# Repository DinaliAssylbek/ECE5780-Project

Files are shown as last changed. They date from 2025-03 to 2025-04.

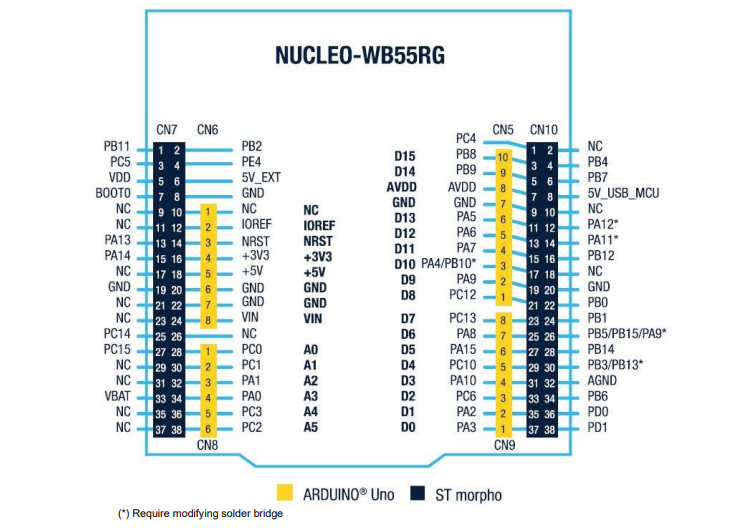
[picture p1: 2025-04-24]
Photos/DEV_Board Pinout.png

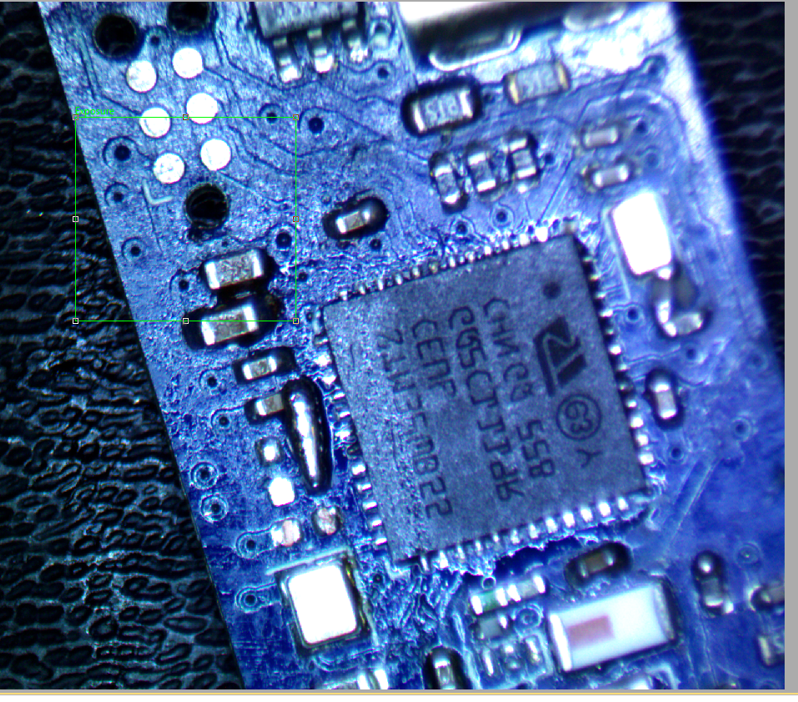
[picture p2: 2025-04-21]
Photos/Screenshot 2025-04-17 140008.png

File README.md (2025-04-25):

Team Members:
Hayden Walpole; Undergraduate; Computer Engineering 
Andy Tran; Undergraduate; Computer Engineering 
Dinali Assylbek; Undergraduate; Computer Engineering
Stein Witt; Undergraduate; Mechanical Engineering

-File Directory-
CAD_FILES: file for the Platic Housing of our Watch Monitor
Datasheetes: BOM and datasheets for the given componants
HealthMonitor: Main Code file to be used to Flash the board with initialization and reading the sensor
Nucleo_Board_Testing: Code used to Test Dev board and Flashing with our 6-pin SWD cable.
PCB: PCB Scematic files and Board Design
Photos: Pictures of the development and debugging process. Also contains helpful refrence photos
Analog Discovery Code Attempts: Code we tried to use to communicate over I2C using Waveform with an analog discovery.

Milestone 4 Powerpoint presentation: https://1drv.ms/p/c/c447666567076377/EbAtq3pLUSZKpYCg5cf9b-IBzeUnjeowH9_FPiCp1k7Zxw?e=1KSI1v

You need to install the following for the STM32 VSCode extension to work.

-STMCubeIDE
-STMCubeMX
-STMCLT
-STMMCU
ECE 5780 – ReadMe Documentation
Project Name: Wearable Health Monitor 
Purpose:
The purpose of this project is to design, assemble, and program a custom PCB for a compact wearable device that allows a person to continuously monitor their heart rate and blood oxygen levels (SpO₂). The device provides real-time feedback when readings fall outside safe thresholds by using an onboard vibrating motor and status LEDs. It is intended to be a low-power, discreet health monitoring solution suitable for everyday use.
Functionality:
The Wearable Health Monitor includes the following features:
•	Real-Time Heart Rate Monitoring: Uses the MAX30102 optical sensor to continuously measure the user’s heart rate.
•	SpO₂ (Blood Oxygen) Monitoring: Calculates and updates the user’s oxygen saturation level every few seconds.
•	Vibration Motor and Status LED: Activates when heart rate or oxygen levels are outside the defined safe range.
•	Power Supply: Currently powered via USB-C. However, the board can run on a battery if connected through the USB-C port (e.g., with a USB-C battery pack).

•	Optional Bluetooth: The board supports Bluetooth; however, Bluetooth functionality is not implemented in the driver code.

Setup Instructions:
1.	PCB Fabrication:
To manufacture the board, use the schematic and PCB layout files found in the PCB directory of the GitHub repository. These files are compatible with common PCB manufacturers such as PCBWay (used for this project). Before submission, make sure to generate and include:
o	Gerber files
o	Bill of Materials (BOM)
o	Pick-and-place files (if needed)
The schematic for this project is presented below: 
 
2.	Assembly Guidelines:
Component assembly is a critical step due to the small form factor and use of QFN or similar packages that do not expose all pins. Many components have pads located underneath, making traditional soldering difficult.
Important:
Avoid using a reflow oven. While convenient, reflow can result in unreliable connections or floating components. Instead:
o	Use solder paste with a precision heat gun
o	Inspect each connection carefully under magnification
However, if your manufacturer offers services for PCB assembly, it is advisable to have them assemble the board for you. This is to avoid any potential problems regarding the PCB itself.
Note: Be careful when handling the board after assembly, the parts are delicate!
3.	Programming the Board:
The board is programmed using a dedicated ST-Link programmer with a 6-pin Tag-Connect cable.
o	To enter bootloader mode:
	Power the board
	Press and hold the BOOT button
	Momentarily ground the NRST (reset) pin (accessible via the ST-Link header)
	Release NRST while continuing to hold BOOT for a few seconds
Note: While USB-C bootloader programming is theoretically possible, it has not been tested. The ST-Link method is the recommended and verified approach.
When using the ST-Link, bootloader mode is not required.
4.	Firmware Setup:
o	Clone the repository and open the Health Monitor project
o	All source files are in the Core directory
o	A custom library for the MAX30102 sensor is included
Pin Configuration:
o	PB8 → I2C1_SCL (Clock Line)
o	PB9 → I2C1_SDA (Data Line)
o	Pin 12 → Controls both the vibration motor and status LED
The project builds and runs best using the STM32CubeIDE and STM32CubeProgrammer.
Once the board is powered and connected via ST-Link:
o	Build the project
o	Flash the firmware using the programmer
o	The device will begin operation immediately after flashing

5.	Troubleshooting
In the case where you may encounter issues with the PCB, there are several steps you can take to diagnose and resolve problems:
o	No Power to the Board:
o	Confirm that the USB-C cable is securely connected and providing power. If not, try to use a different cable to supply power to the chip
o	Check the voltages along all the voltage lines (3.3V and 1.8V) using a multimeter.
o	Ensure all power-related components (LDO regulator, bypass caps, etc.) are properly soldered. If the board starts to heat up rapidly, use a thermal camera to help check for shorts.
o	Sensor Not Detected (MAX30102):
o	Double-check I2C connections (PB8 for SCL, PB9 for SDA).
o	Use a logic analyzer or oscilloscope to verify I2C traffic.
o	Confirm the sensor that the registers and addresses are configured correctly.
o	Programming Issues:
o	Make sure the ST-Link is correctly connected via the Tag-Connect header.
o	Ensure that the Tag-Connect and ST-Link work. This can be achieved by uploading code to a breakout board.
o	Ensure that all user code lies in the correct regions as defined in the cube IDE. Check that all the correct header files are included and desired code is not commented out.
o	Miscellaneous Issues:
o	If the PCB fails to work, inspect solder joints again for bridges or incomplete connections. Examine under a microscope. If possible, reach out to someone with a more trained eye to look at the soldering job.
o	Make sure components on the board are assembled correctly. This means making sure the orientations of the components are in the right place, and no components are missing.
o	Be careful when disconnecting the cable when flashing the board. This potentially could cause you to brick the chip on the PCB. 

Videos Used as Refrences:
Schematic Design Video: https://www.youtube.com/watch?v=nkHFoxe0mrU
PBC Design Video: https://www.youtube.com/watch?v=PlXd3lLZ4vc&t=10184s

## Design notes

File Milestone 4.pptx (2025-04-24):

## MILESTONE 1 UPDATE: Integrating Machine Learning Into UTAP App

<N

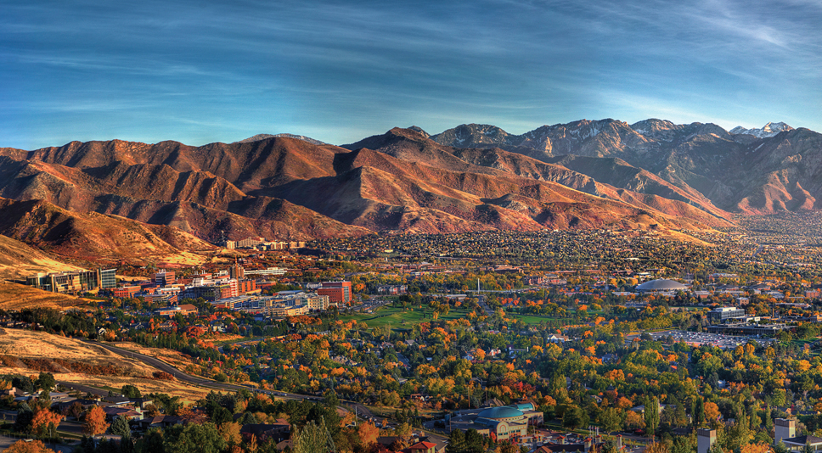
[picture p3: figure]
Campus Fall Panorama

Hayden Walpole and Daniel McNally
Technical Advisor: Nathan Hansen & Prof. Benjamin Sanchez

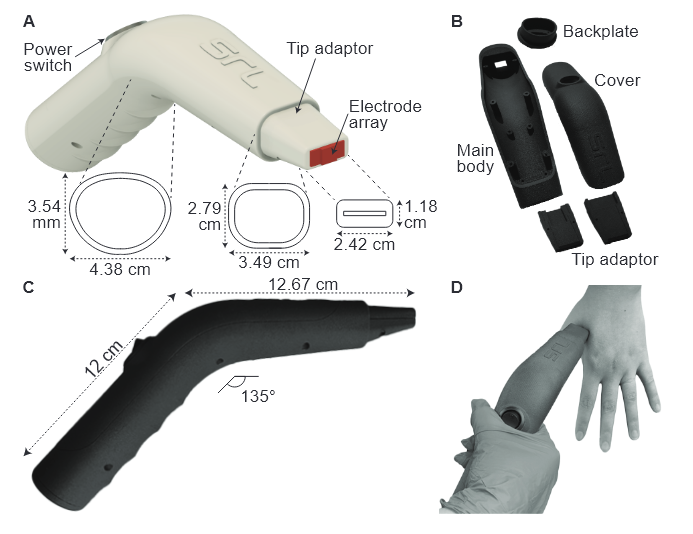
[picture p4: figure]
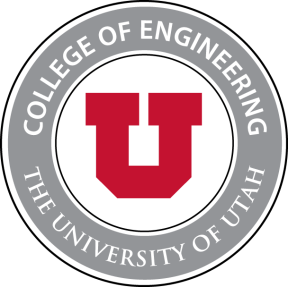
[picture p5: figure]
ENG_SEAL_RedGray

## MILESTONE 1 UPDATE: Integrating Machine Learning Into URSKIN App

<N

Hayden Walpole and Daniel McNally
Technical Advisor: Nathan Hansen & Prof. Benjamin Sanchez

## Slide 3

Our Timeline

Milestone | Estimated Completion
Working Frontend UI | March 15th, 2025
Single Model ML Prototype | April 15th, 2025
Multiple Model ML Application | September 1st, 2025
Final Integrated Application | November 1st, 2025
Demo Day | December 5th, 2025

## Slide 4

Team Contributions

Daniel

User Interface

ONNX Implementation

Hayden

Research: Conversion Tools

Models used in Project
(Slide 8)

CITI Bio-Medical Research Training for Data Collection

ADABoosting Model Testing:
-Default Data Array
-Measure Data from Device

FUTURE:
Data Collection
UI Finalization
Electrode Array Improvement
Individual Model Type Implementation

FUTURE:
Data Collection
Results validation and comparison to PC model
Unit Testing
Multi-Prediction Model

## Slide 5

Original User Interface

User interface changes

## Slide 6

Original User Interface

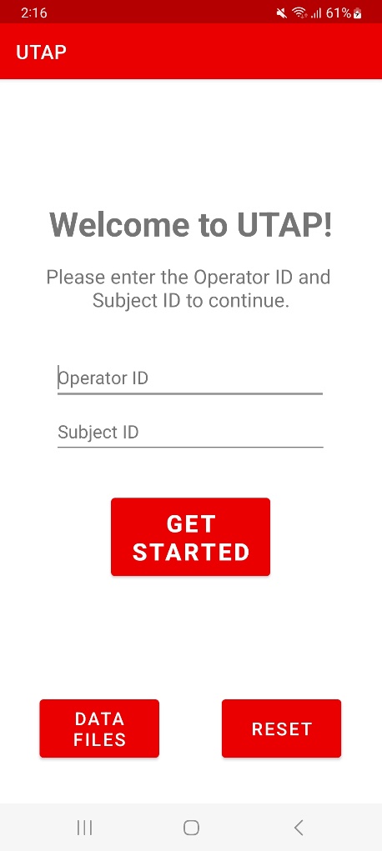
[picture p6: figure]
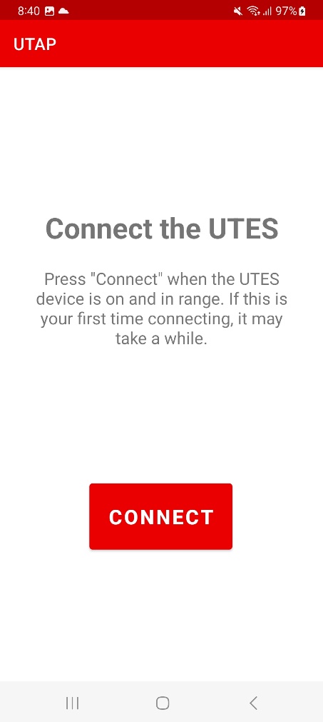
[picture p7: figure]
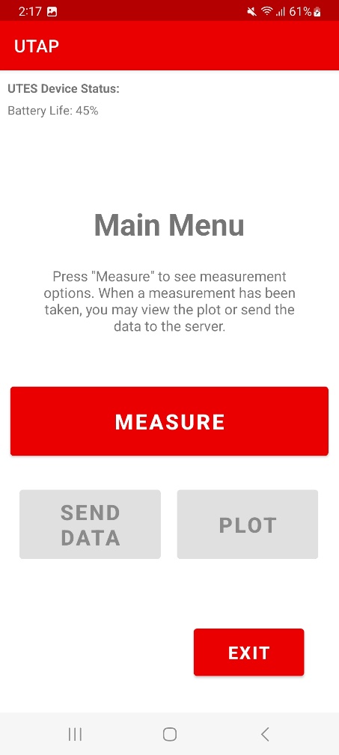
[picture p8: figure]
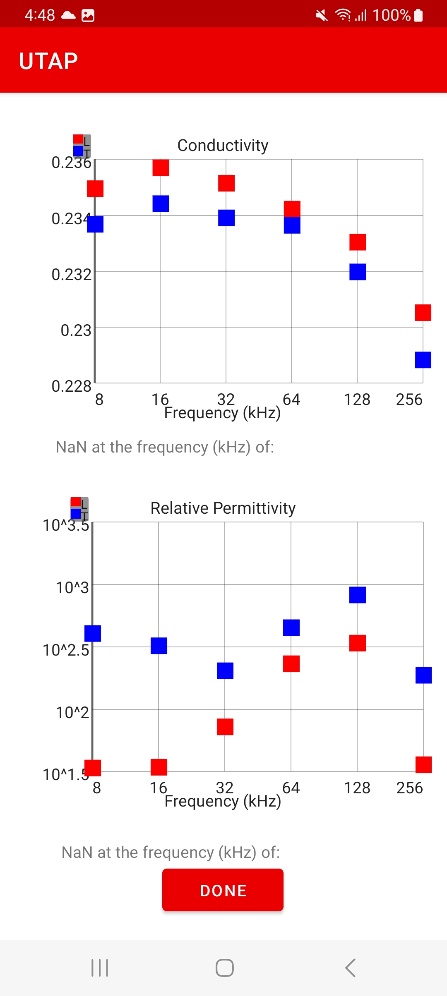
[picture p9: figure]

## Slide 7

New User Interface

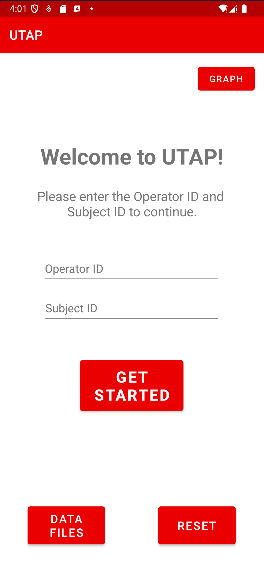
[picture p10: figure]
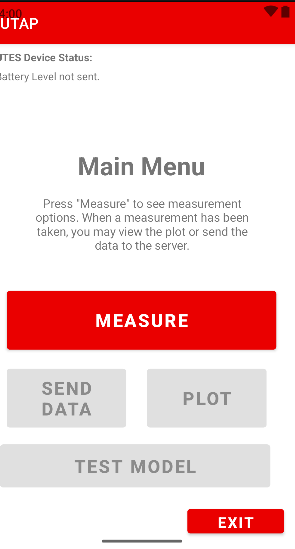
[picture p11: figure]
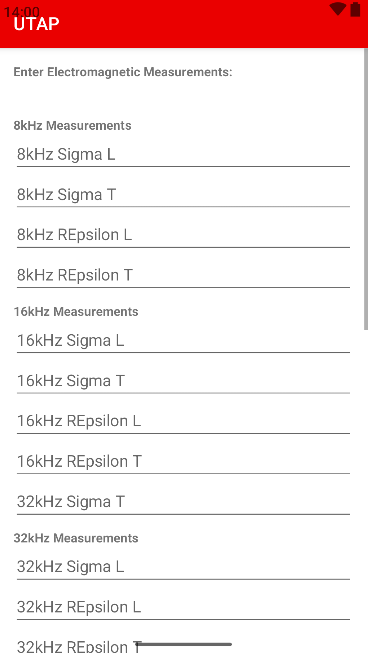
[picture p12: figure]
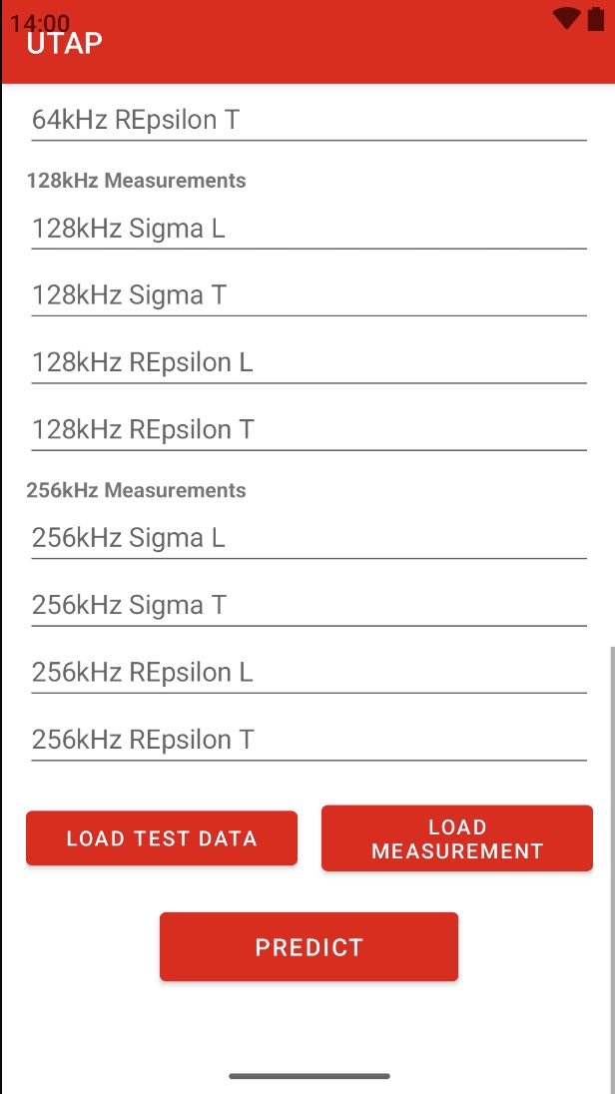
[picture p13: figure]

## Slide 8

Original User Interface

Single Model ML Prototype

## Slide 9

Machine Learning Models Involved

- KNN
- Decision Trees
- Naive Bayes
- Logistic Regression
- Support Vector Machine
- Random Forest
- Adaboosting (base model decision tree stumps)
- Extreme Gradient Boosting (base model decision tree stumps)
- Gradient Boosting (base model decision tree stumps)
- Bagged decision trees
- Voting (based on the best three performing models for each comparison)
- Stacking (based on the best three performing models for each comparison)

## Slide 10

Transferring ML from Python to Mobile app

- One of the first challenges we faced was finding the right conversion process to implement the existing models in Python into our mobile application.
- We decided to use ONNX since it is well documented and well supported for our needs.

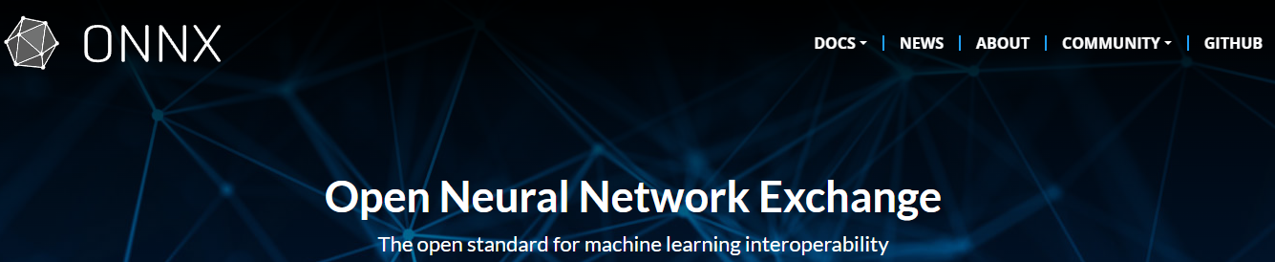
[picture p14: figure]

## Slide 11

Code: Graph Activity

- This was a new class activity we created to import and manage the Models we import from ONNX.

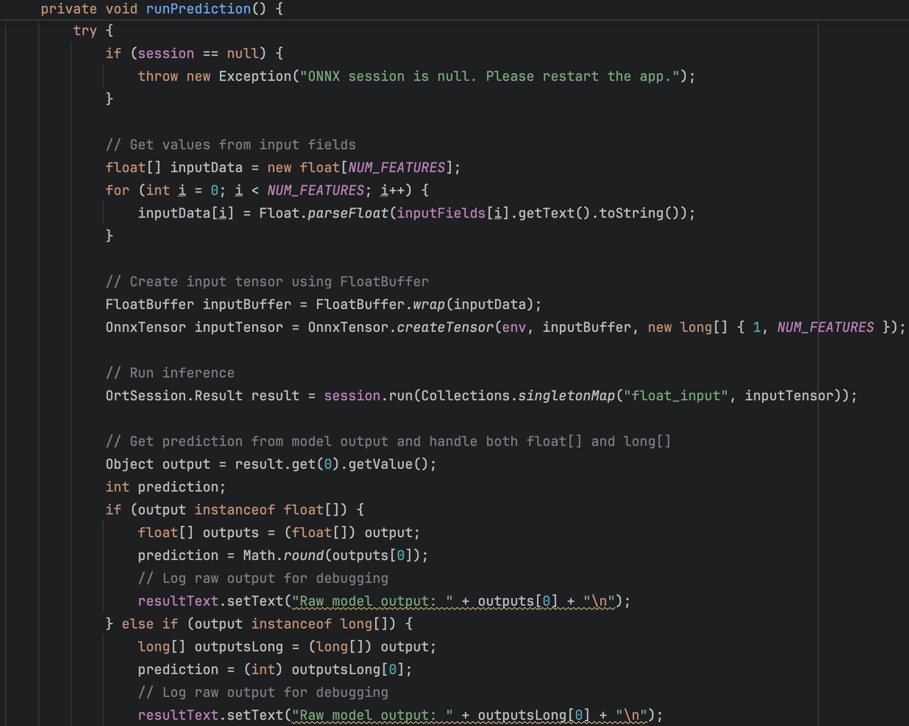
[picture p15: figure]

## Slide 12

Data File

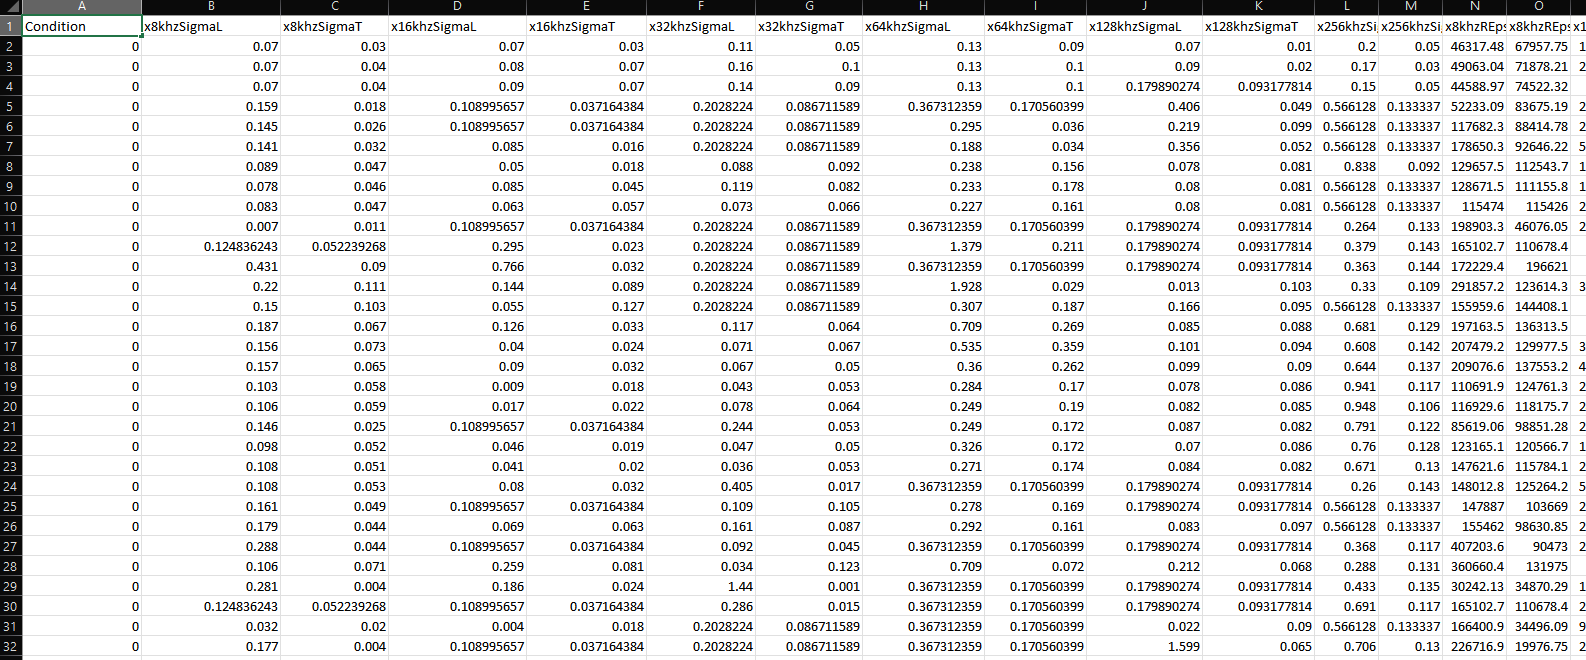
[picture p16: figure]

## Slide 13

Thank You!

ADA BOOSTING DEMO
Healthy Vs SCC

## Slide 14

Plans going Forward

- Our next Steps will be to refine the User interface and integrate more models.
- The models are mostly 1 vs 1 Comparison, so multiple models are required to run the comparisons at once to get the final Prediction.

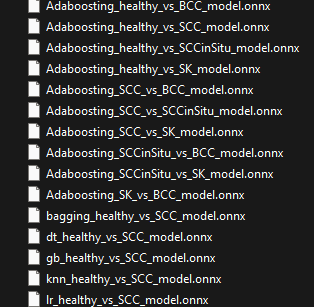
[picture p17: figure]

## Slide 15

Thank You!

Questions?

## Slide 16

Image Sources:

- Images from ONNX mainpage found at https://onnx.ai/
- Images from “UTES Training Guide V6” PowerPoint created by Nathan Hansen
- Images from materials from the Sanchez Research Lab UTES Device Resources and Publications

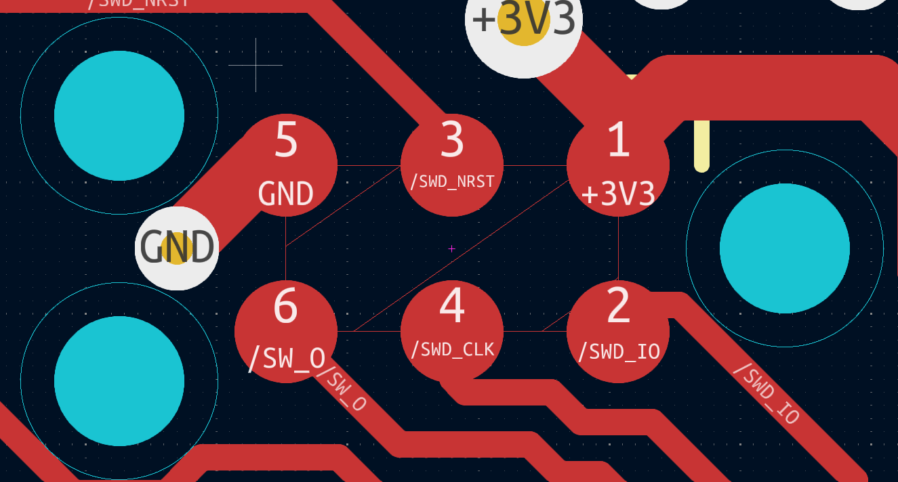
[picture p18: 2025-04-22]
Photos/6-Pin SWD pins.png

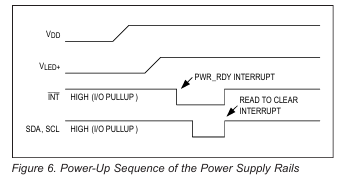
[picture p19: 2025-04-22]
Photos/Sensor Power-up Sequence.png

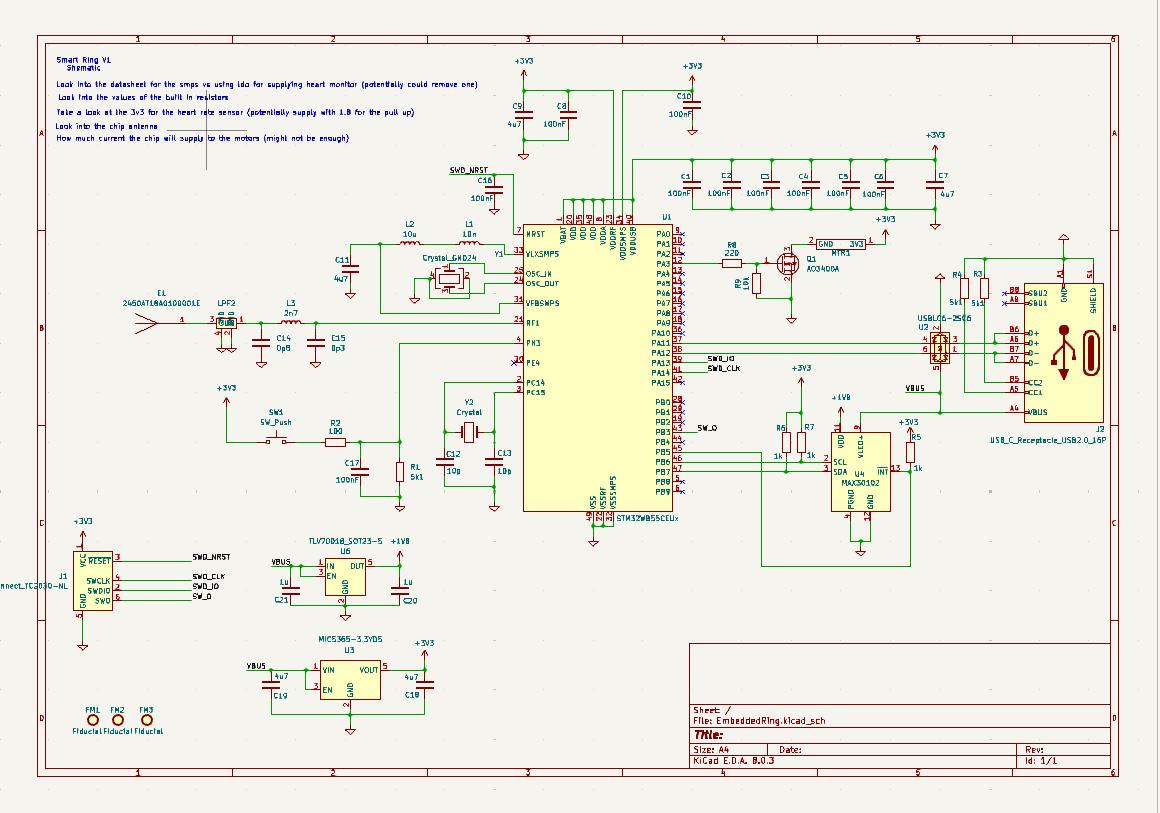
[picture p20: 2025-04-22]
Photos/Full Schemeatic Diagram.png

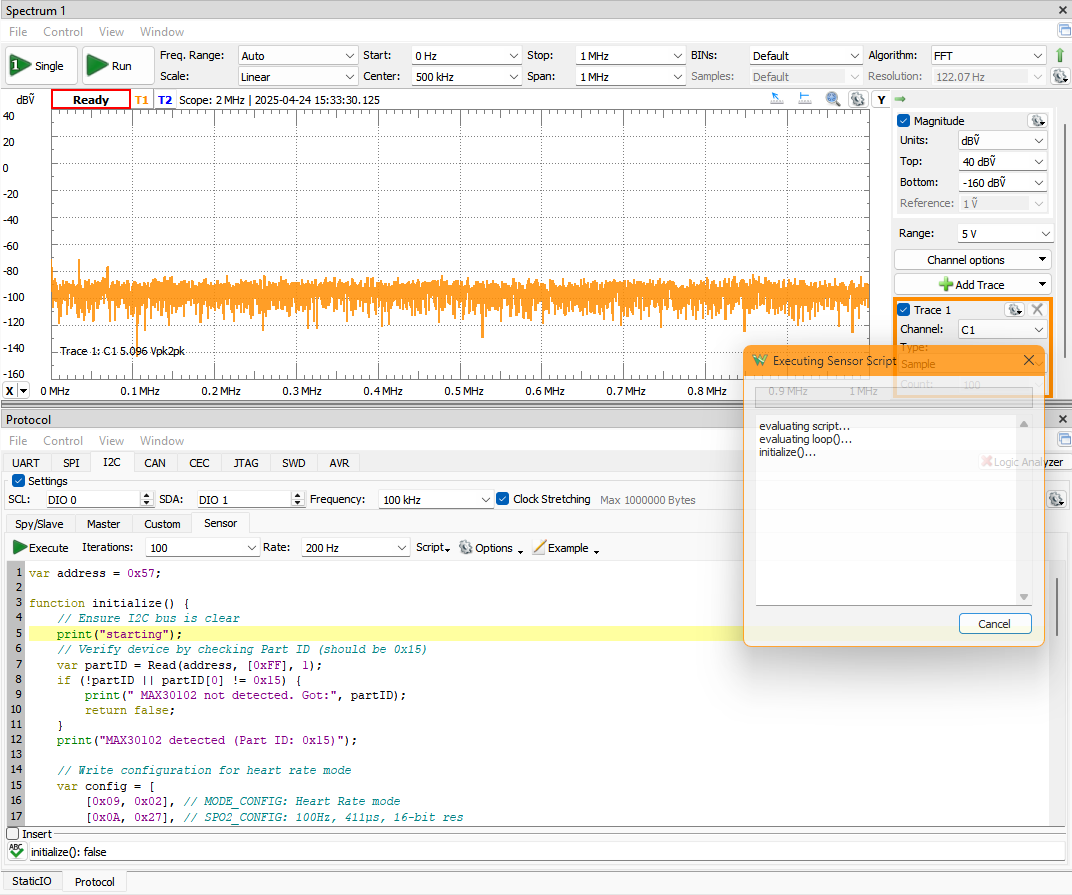
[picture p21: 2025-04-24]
Photos/Analog Waveform I2C attempt.png

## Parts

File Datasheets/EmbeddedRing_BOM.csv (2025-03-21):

Reference | Value | Datasheet | Footprint | Qty | DNP | Distributer Link | Manufacturer | Manufacturer Part Number
LPF2,MTR1 | ~ |  | -- mixed values -- | 2 |  | -- mixed values -- | -- mixed values -- | -- mixed values --
C20,C21 | 1u | ~ | Capacitor_SMD:C_0201_0603Metric_Pad0.64x0.40mm_HandSolder | 2 |  | https://www.digikey.com/en/products/detail/nextgen-components/0603B105K100XD/18677009 | Aillen | 0603B105K100XD
Q1 | AO3400A | http://www.aosmd.com/pdfs/datasheet/AO3400A.pdf | Package_TO_SOT_SMD:SOT-23 | 1 |  | https://www.digikey.com/en/products/detail/alpha-omega-semiconductor-inc/AO3400A/1855772 | Alpha & Omega Semiconductor Inc. | AO3400A
U4 | MAX30102 | https://datasheets.maximintegrated.com/en/ds/MAX30102.pdf | low_pass_filter:heart_rate_sensor | 1 |  | https://www.digikey.com/en/products/detail/analog-devices-inc-maxim-integrated/MAX30102EFD-T/6188734 | Analog Devices Inc./Maxim Integrated | MAX30102EFD+T
SW1 | SW_Push | ~ | Button_Switch_SMD:SW_SPST_CK_RS282G05A3 | 1 |  | https://www.digikey.com/en/products/detail/c-k/RS-282G05A3-SM-RT/2747190?s=N4IgTCBcDaIE4GcwA4wHMAMBWAhgZgQFs4AXEAXQF8g | C&K | RS-282G05A3-SM RT
J2 | USB_C_Receptacle_USB2.0_16P | https://www.usb.org/sites/default/files/documents/usb_type-c.zip | Connector_USB:USB_C_Receptacle_GCT_USB4085 | 1 |  | https://www.digikey.com/en/products/detail/gct/USB4085-GF-A/9859662 | GCT | USB4085-GF-A
E1 | 2450AT18A0100001E |  | low_pass_filter:antennaa | 1 |  | https://www.digikey.com/en/products/detail/johanson-technology-inc/2450at18a0100001e/1560676 | Johanson Technology Inc. | 2450AT18A0100001E
C1,C2,C3,C4,C5,C6,C8,C10,C16,C17 | 100nF | ~ | Capacitor_SMD:C_0402_1005Metric | 10 |  | https://www.digikey.com/en/products/detail/kyocera-avx/04026c104kat2a/2345263 | KYOCERA AVX | 04026C104KAT2A
C7,C9,C11,C18,C19 | 4u7 | ~ | -- mixed values -- | 5 |  | https://www.digikey.com/en/products/detail/kyocera-avx/0603YD475MAT2A/9748484?s=N4IgTCBcDaIAwDY4GYCeATALAdgKwFkBDAFzEJAF0BfIA | KYOCERA AVX | 0603YD475MAT2A
C12,C13 | 10p | ~ | Capacitor_SMD:C_01005_0402Metric | 2 |  | https://www.digikey.com/en/products/detail/kyocera-avx/KGM05ACG1H100JN/11258418?s=N4IgTCBcDaIAwBY5gKwEMCMc4Cs0BcE0QBdAXyA | KYOCERA AVX | KGM05ACG1H100JN
U3 | MIC5365-3.3YD5 | http://ww1.microchip.com/downloads/en/DeviceDoc/mic5365.pdf | Package_TO_SOT_SMD:SOT-23-5 | 1 |  | https://www.digikey.com/en/products/detail/microchip-technology/mic5365-3-3yd5-tr/3671879 | Microchip Technology | MIC5365-3.3YD5-TR
C14 | 0p8 | ~ | Capacitor_SMD:C_01005_0402Metric | 1 |  | https://www.digikey.com/en/products/detail/murata-electronics/GRM1555C1HR80BA01D/3694062 | Murata Electronics | GRM1555C1HR80BA01D
C15 | 0p3 | ~ | Capacitor_SMD:C_01005_0402Metric | 1 |  | https://www.digikey.com/en/products/detail/murata-electronics/GRM1555C1HR30WA01D/3694052 | Murata Electronics | GRM1555C1HR30WA01D
L1 | 10n | ~ | Inductor_SMD:L_0402_1005Metric | 1 |  | https://www.digikey.com/en/products/detail/murata-electronics/lqg15wz10nj02d/6798669 | Murata Electronics | LQG15WZ10NJ02D
L2 | 10u | ~ | Inductor_SMD:L_0402_1005Metric | 1 |  | https://www.digikey.com/en/products/detail/murata-electronics/lqm21fn100m70l/1016188 | Murata Electronics | LQM21FN100M70L
L3 | 2n7 | ~ | Inductor_SMD:L_01005_0402Metric | 1 |  | https://www.digikey.com/en/products/detail/murata-electronics/LQG15HS2N7S02D/662864?s=N4IgTCBcDaIDYEcDmBGArACwM5gHYHYsAGCAXQF8g | Murata Electronics | LQG15HS2N7S02D
Y1 | Crystal_GND24 | ~ | low_pass_filter:32M_Crystal | 1 |  | https://www.digikey.com/en/products/detail/ndk-nihon-dempa-kogyo-co-ltd/CS06465-32M/7645290 | NDK (NIHON DEMPA KOGYO CO., LTD) | CS06465-32M
Y2 | Crystal | ~ | low_pass_filter:32k_Crystal | 1 |  | https://www.digikey.com/en/products/detail/ndk-nihon-dempa-kogyo-co-ltd/STDMUB1-32-768K/4914433 | NDK (NIHON DEMPA KOGYO CO., LTD) | STDMUB1-32.768K
U1 | STM32WB55CEUx | https://www.st.com/resource/en/datasheet/stm32wb55ce.pdf | low_pass_filter:stm32wb55 | 1 |  | https://www.digikey.com/en/products/detail/stmicroelectronics/STM32WB55CEU6/9919555 | STMicroelectronics | STM32WB55CEU6
U2 | USBLC6-2SC6 | https://www.st.com/resource/en/datasheet/usblc6-2.pdf | Package_TO_SOT_SMD:SOT-23-6 | 1 |  | https://www.digikey.com/en/products/detail/stmicroelectronics/USBLC6-2SC6/1040559 | STMicroelectronics | USBLC6-2SC6
U6 | TLV70018_SOT23-5 | http://www.ti.com/lit/ds/symlink/tlv700.pdf | Package_TO_SOT_SMD:SOT-23-5 | 1 |  | https://www.digikey.com/en/products/detail/texas-instruments/TLV77318PDBVR/23331424 | Texas Instruments | TLV77318PDBVR
R1,R3,R4 | 5k1 | ~ | Resistor_SMD:R_0402_1005Metric | 3 |  | https://www.digikey.com/en/products/detail/yageo/RC0603FR-075K1L/727268?s=N4IgTCBcDaIE4GMAMA2JBmAZnAtEg7AKwDWAjADYgC6AvkA | YAGEO | RC0603FR-075K1L
R2 | 100 | ~ | Resistor_SMD:R_0402_1005Metric | 1 |  | https://www.digikey.com/en/products/detail/yageo/RC0402JR-07100RL/726415 | YAGEO | RC0402JR-07100RL
R5,R6,R7 | 1k | ~ | Resistor_SMD:R_0402_1005Metric | 3 |  | https://www.digikey.com/en/products/detail/yageo/RC0402JR-071KL/726408 | YAGEO | RC0402JR-071KL
R8 | 220 | ~ | Resistor_SMD:R_0402_1005Metric | 1 |  | https://www.digikey.com/en/products/detail/yageo/RC0402JR-07100RL/726415 | YAGEO | RC0402JR-07100RL
R9 | 10k | ~ | Resistor_SMD:R_0402_1005Metric | 1 |  | https://www.digikey.com/en/products/detail/yageo/RC0402JR-07100RL/726415 | YAGEO | RC0402JR-07100RL

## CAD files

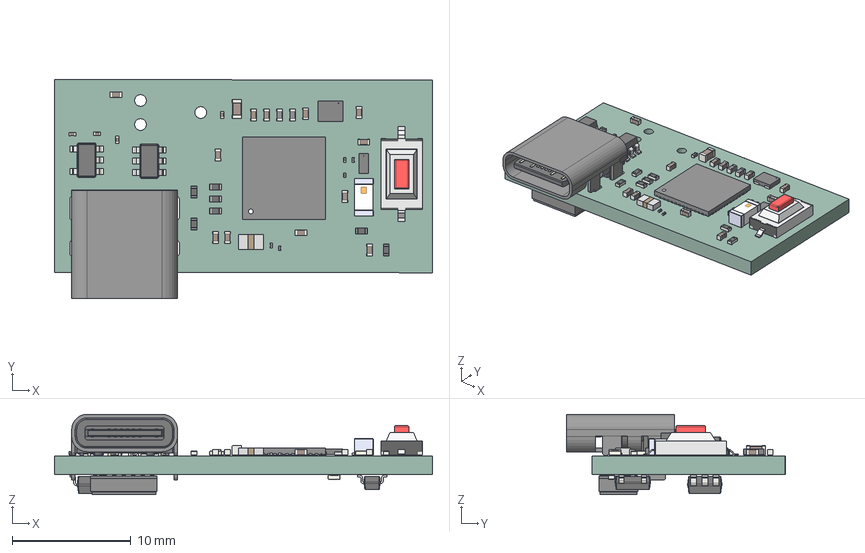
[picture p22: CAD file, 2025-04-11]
CAD_Files/EmbeddedRing.step
31.9 x 18.5 x 6.78 mm
L_01005_0402Metric
L_0402_1005Metric x 2
SOT_23_5 x 2
C_01005_0402Metric x 4
C_0402_1005Metric x 12
R_0402_1005Metric x 9
SW_SPST_CK_RS282G05A3
C_0603_1608Metric
C_0201_0603Metric x 4
USB_C_Receptacle_GCT_USB4085
2450AT18A0100001E
STM32WB55CGU6
SOT_23_6
MAX30102EFD+
SOT_23
EmbeddedRing_PCB

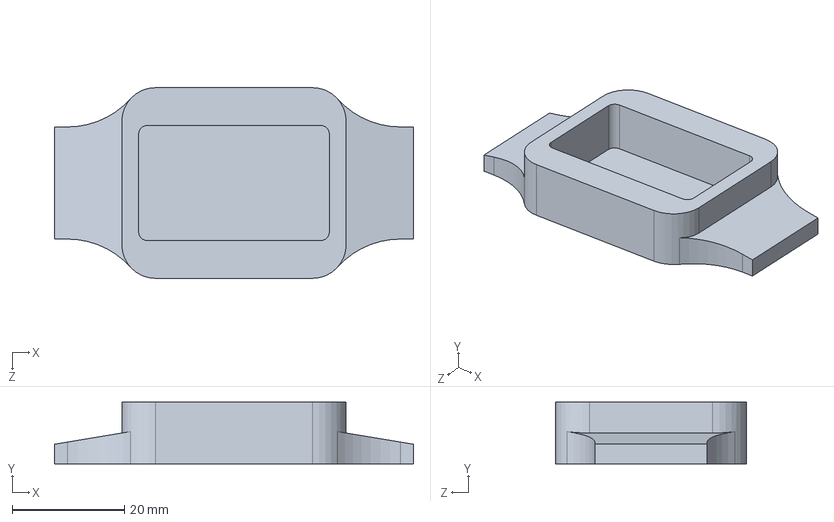
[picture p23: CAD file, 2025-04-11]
CAD_Files/Case.SLDPRT
64.0 x 11.0 x 34.0 mm

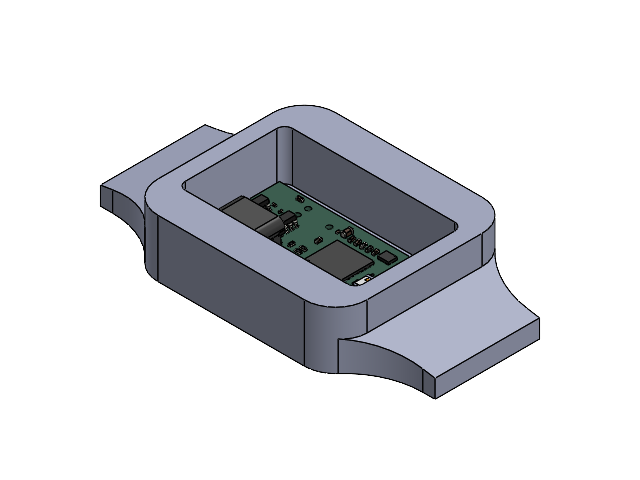
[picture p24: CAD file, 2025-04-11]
CAD_Files/CaseAndBoard.SLDASM
Case
L_01005_0402Metric-0.step
L_0402_1005Metric-1.step x 2
SOT_23_5.step x 2
C_01005_0402Metric-2.step x 4
C_0402_1005Metric-3.step x 12
R_0402_1005Metric-4.step x 9
part.step
SW_SPST_CK_RS282G05A3-5.step
C_0603_1608Metric-6.step
part-7.step
C_0201_0603Metric-8.step x 4
part-9.step
USB_C_Receptacle_GCT_USB4085-10.step
2450AT18A0100001E-11.step
STM32WB55CGU6.step
SOT_23_6.step
MAX30102EFD+.step
SOT_23.step
EmbeddedRing_PCB.step

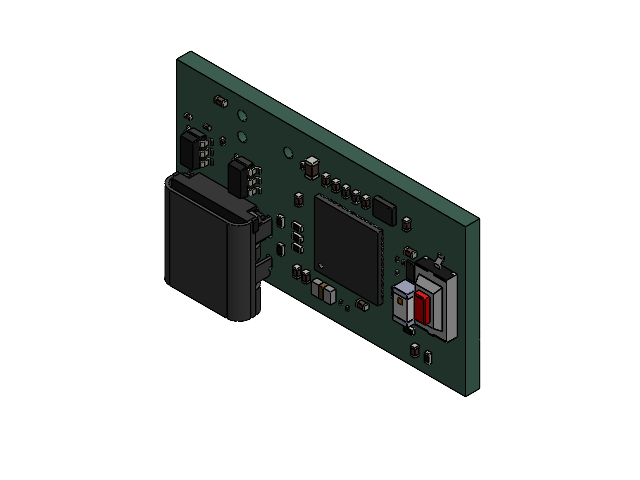
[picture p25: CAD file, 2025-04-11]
CAD_Files/Board.SLDASM
L_01005_0402Metric-0.step
L_0402_1005Metric-1.step x 2
SOT_23_5.step x 2
C_01005_0402Metric-2.step x 4
C_0402_1005Metric-3.step x 12
R_0402_1005Metric-4.step x 9
part.step
SW_SPST_CK_RS282G05A3-5.step
C_0603_1608Metric-6.step
part-7.step
C_0201_0603Metric-8.step x 4
part-9.step
USB_C_Receptacle_GCT_USB4085-10.step
2450AT18A0100001E-11.step
STM32WB55CGU6.step
SOT_23_6.step
MAX30102EFD+.step
SOT_23.step
EmbeddedRing_PCB.step

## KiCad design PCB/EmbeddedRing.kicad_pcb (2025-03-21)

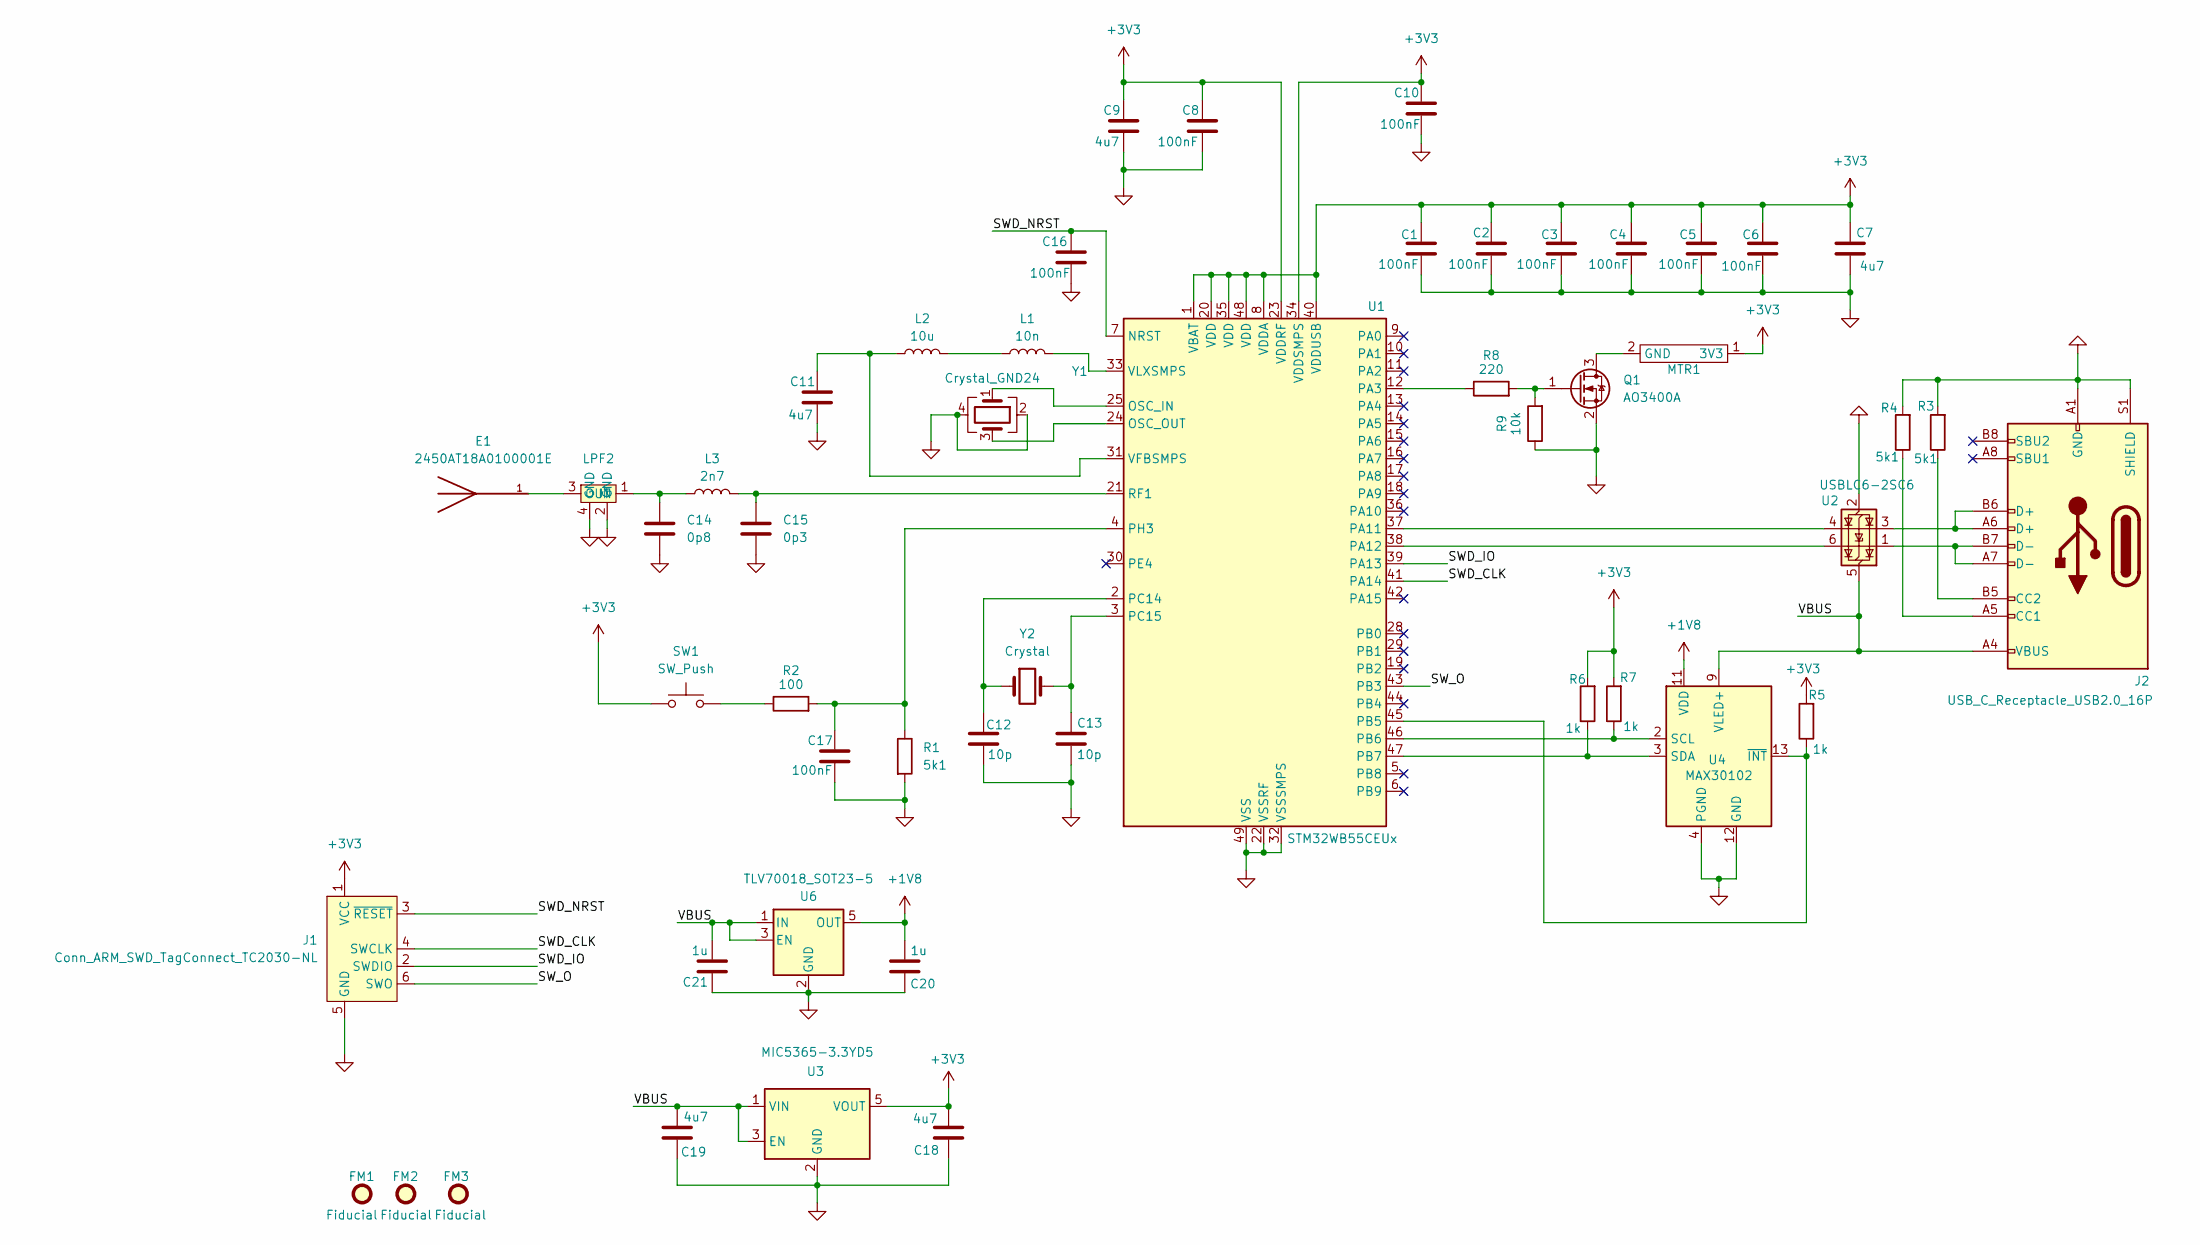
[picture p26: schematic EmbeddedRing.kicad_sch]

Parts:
C1, C2, C3, C4, C5, C6, C8, C10, C16, C17: 100nF; C_0402_1005Metric; Manufacturer Part Number 04026C104KAT2A
C7: 4u7; C_0603_1608Metric; Manufacturer Part Number 0603YD475MAT2A
C9, C11: 4u7; C_0402_1005Metric_Pad0.74x0.62mm_HandSolder; Manufacturer Part Number 0603YD475MAT2A
C12, C13: 10p; C_01005_0402Metric; Manufacturer Part Number KGM05ACG1H100JN
C14: 0p8; C_01005_0402Metric; Manufacturer Part Number GRM1555C1HR80BA01D
C15: 0p3; C_01005_0402Metric; Manufacturer Part Number GRM1555C1HR30WA01D
C18, C19: 4u7; C_0201_0603Metric_Pad0.64x0.40mm_HandSolder; Manufacturer Part Number 0603YD475MAT2A
C20, C21: 1u; C_0201_0603Metric_Pad0.64x0.40mm_HandSolder; Manufacturer Part Number 0603B105K100XD
E1: 2450AT18A0100001E; antennaa; PARTREV 4.0
FM1, FM2, FM3: Fiducial; Fiducial_0.5mm_Mask1.5mm
J1: Conn_ARM_SWD_TagConnect_TC2030-NL; Tag-Connect_TC2030-IDC-NL_2x03_P1.27mm_Vertical
J2: USB_C_Receptacle_USB2.0_16P; USB_C_Receptacle_GCT_USB4085; Manufacturer Part Number USB4085-GF-A
L1: 10n; L_0402_1005Metric; Manufacturer Part Number LQG15WZ10NJ02D
L2: 10u; L_0402_1005Metric; Manufacturer Part Number LQM21FN100M70L
L3: 2n7; L_01005_0402Metric; Manufacturer Part Number LQG15HS2N7S02D
LPF2: low-pass_filter-footprint; Manufacturer Part Number DLF162500LT-5028A1
MTR1: motor pad
Q1: AO3400A; SOT-23; Manufacturer Part Number AO3400A
R1, R3, R4: 5k1; R_0402_1005Metric; Manufacturer Part Number RC0603FR-075K1L
R2: 100; R_0402_1005Metric; Manufacturer Part Number RC0402JR-07100RL
R5, R6, R7: 1k; R_0402_1005Metric; Manufacturer Part Number RC0402JR-071KL
R8: 220; R_0402_1005Metric; Manufacturer Part Number RC0402JR-07100RL
R9: 10k; R_0402_1005Metric; Manufacturer Part Number RC0402JR-07100RL
SW1: SW_Push; SW_SPST_CK_RS282G05A3; Manufacturer Part Number RS-282G05A3-SM RT
U1: STM32WB55CEUx; stm32wb55; Manufacturer Part Number STM32WB55CEU6
U2: USBLC6-2SC6; SOT-23-6; Manufacturer Part Number USBLC6-2SC6
U3: MIC5365-3.3YD5; SOT-23-5; Manufacturer Part Number MIC5365-3.3YD5-TR
U4: MAX30102; heart_rate_sensor; Manufacturer Part Number MAX30102EFD+T
U6: TLV70018_SOT23-5; SOT-23-5; Manufacturer Part Number TLV77318PDBVR
Y1: Crystal_GND24; 32M_Crystal; Manufacturer Part Number CS06465-32M
Y2: Crystal; 32k_Crystal; Manufacturer Part Number STDMUB1-32.768K

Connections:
+1V8: C20.1, U4.11 (VDD), U6.5 (OUT)
+3V3: C1.1, C2.1, C3.1, C4.1, C5.1, C6.1, C7.1, C8.1, C9.1, C10.1, C18.1, J1.1 (VCC), MTR1.1 (3V3), R5.2, R6.2, R7.2, SW1.1, U1.1 (VBAT), U1.8 (VDDA), U1.20 (VDD), U1.23 (VDDRF), U1.34 (VDDSMPS), U1.35 (VDD), U1.40 (VDDUSB), U1.48 (VDD), U3.5 (VOUT)
/SWD_CLK: J1.4 (SWCLK), U1.41 (PA14)
/SWD_IO: J1.2 (SWDIO), U1.39 (PA13)
/SWD_NRST: C16.1, J1.3 (~RESET), U1.7 (NRST)
/SW_O: J1.6 (SWO), U1.43 (PB3)
/VBUS: C19.1, C21.1, J2.A4 (VBUS), J2.A9 (VBUS), J2.B4 (VBUS), J2.B9 (VBUS), U2.5 (VBUS), U3.1 (VIN), U3.3 (EN), U4.9 (VLED+), U4.10 (VLED+), U6.1 (IN), U6.3 (EN)
GND: C1.2, C2.2, C3.2, C4.2, C5.2, C6.2, C7.2, C8.2, C9.2, C10.2, C11.2, C12.2, C13.2, C14.2, C15.2, C16.2, C17.2, C18.2, C19.2, C20.2, C21.2, J1.5 (GND), J2.A1 (GND), J2.A12 (GND), J2.B1 (GND), J2.B12 (GND), J2.S1 (SHIELD), LPF2.2 (GND), LPF2.4 (GND), Q1.2 (S), R1.2, R3.2, R4.2, R9.1, U1.22 (VSSRF), U1.32 (VSSSMPS), U1.49 (VSS), U2.2 (GND), U3.2 (GND), U4.4 (PGND), U4.12 (GND), U6.2 (GND), Y1.2, Y1.4
unnamed: J2.A5 (CC1), R4.1
unnamed: J2.B5 (CC2), R3.1
unnamed: J2.A6 (D+), J2.B6 (D+), U2.3 (I/O2)
unnamed: J2.A7 (D-), J2.B7 (D-), U2.1 (I/O1)
unnamed: L1.1, L2.2
unnamed: C14.1, L3.1, LPF2.1 (IN)
unnamed: E1.1, LPF2.3 (OUT)
unnamed: MTR1.2 (GND), Q1.3 (D)
unnamed: Q1.1 (G), R8.2, R9.2
unnamed: R2.1, SW1.2
unnamed: U1.25 (OSC_IN), Y1.1
unnamed: U1.24 (OSC_OUT), Y1.3
unnamed: R8.1, U1.12 (PA3)
unnamed: U1.37 (PA11), U2.4 (I/O2)
unnamed: U1.38 (PA12), U2.6 (I/O1)
unnamed: R5.1, U1.45 (PB5), U4.13 (~INT)
unnamed: R7.1, U1.46 (PB6), U4.2 (SCL)
unnamed: R6.1, U1.47 (PB7), U4.3 (SDA)
unnamed: C12.1, U1.2 (PC14), Y2.1
unnamed: C13.1, U1.3 (PC15), Y2.2
unnamed: C17.1, R1.1, R2.2, U1.4 (PH3)
unnamed: C15.1, L3.2, U1.21 (RF1)
unnamed: C11.1, L2.1, U1.31 (VFBSMPS)
unnamed: L1.2, U1.33 (VLXSMPS)

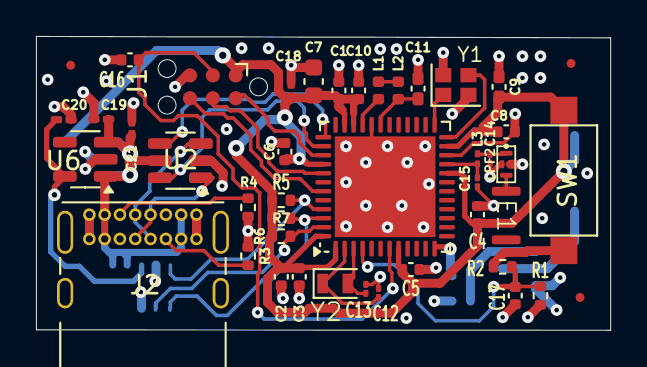
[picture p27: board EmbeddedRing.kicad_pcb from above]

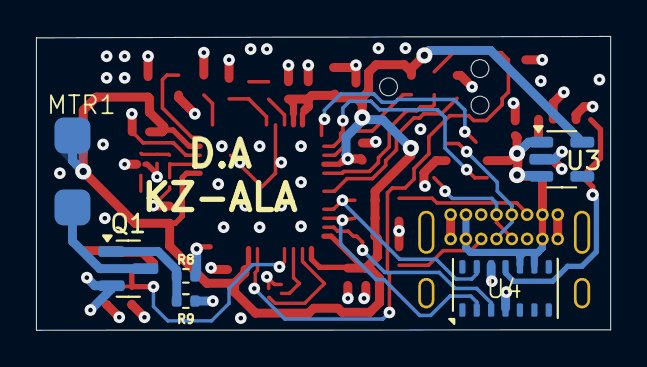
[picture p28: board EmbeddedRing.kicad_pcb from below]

Board: 4 copper layers, 31.9 x 16.3 mm, 50 parts (6 on the bottom side), 32 nets.

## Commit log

2025-04-02 Got LED blinking using STM32 CubeIDE
2025-04-11 Added CAD models folder and started designing enclosure in SolidWorks
    [Board.SLDASM, Case.SLDPRT, CaseAndBoard.SLDASM, EmbeddedRing.step]
2025-04-22 psuedo code for reading data from hr sensor
2025-04-24 Tried using analog discovery to talk to the Sensor, added code attempt to repo
